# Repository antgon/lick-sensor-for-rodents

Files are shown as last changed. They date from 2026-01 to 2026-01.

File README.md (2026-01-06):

banner

# Lick sensor for rodents

A device for measuring licking behaviour in rodents in real time.

This project describes a lick sensor developed for the purpose of
measuring licking behaviour in laboratory animals. Licking behaviour,
and in particular the analysis of lick microstructure, is a useful tool
for studying ingestive behaviour, motivation, and food preference.

2021-2025 Antonio González

## Features

The lick sensor is built with a Raspberry Pi Pico microcontroller board
and a capacitive touch sensor. It can can be used with standard water
bottles for rodents, and does not require modifications to animal home
cages. The lick sensor can thus be adapted to a wide range of
experimental setups.

Licks are detected in real time with millisecond precision from one or
many drink bottles simultaneously. The data can be recorded using any
standard data acquisition system; it can be sent to a computer for
storage; and/or it can be used for real-time control of additional
laboratory hardware such as LEDs for optogenetics.

Overview of lick sensor

### Variants

Different variants of the lick sensor are possible, depending on the
number of drink bottles required, and also on whether lick data is to be
recorded "raw" (i.e. as a continuous vector of on/off, digital data
samples), or saved in the form of lick events (timestamps).

Details of each of these options can be found in the relevant
directories. Briefly,

* [**One bottle, one BNC output**](bottle-x1-bnc-out). This is the
  simplest lick sensor variant: it uses only one drink bottle. Licks
  from this bottle are detected and directed to a BNC connector from
  where they can be recorded with a data acquisition system and/or used
  for driving additional laboratory hardware in real time.

* [**Several bottles, BNC outputs**](bottle-x6-bnc-out). Similar to the
  setup above but using more than one drink bottle.

* [**Many bottles (up to 12), USB output**](bottle-x12-usb-out). Here,
  lick events (timestamps) from many drink bottles are detected and sent
  to a computer connected to the microcontroller with a USB cable. The
  construction of this lick sensor is very simple and a data-acquisition
  system is not required. On the other hand, the software side of it is
  more elaborate: it is necessary to install and run Python software in
  the host computer.

* [**Many bottles (up to 24), USB output**](bottle-x24-usb-out). As
  above, but using 2 touch-detection boards to handle up to 24 drink
  bottles simultaneously.

## Requirements

### Lick sensor hardware

* Drinking bottle(s). Any standard drinking bottle for rodents should
  work. We use the Crystal Deluxe Mini Bottle 75 ml ([Classic Pet
  Products, UK, cat. num.
  0190](https://classicpetproducts.co.uk/product/crystal-deluxe-mini-bottle-75ml/))
  obtained from a local pet shop.
* [Raspberry Pi
  Pico](https://www.raspberrypi.com/products/raspberry-pi-pico)
  microcontroller board.
* Capacitive touch sensor module. We use [Adafruit product ID
  1982](https://www.adafruit.com/product/1982); up to 12 water bottles
  can be connected to one of these modules[^1]. Other manufacturers sell
  touch sensors based on the MPR121 and any of these should work equally
  well.
* Stranded-core cable (e.g. 24 AWG or 26 AWG standard hook-up cable).
* A USB cable for the Raspberry Pi Pico.
* BNC connector(s). Optional, depending on the sensor variant chosen.

Some means to put the components together, for example:

* Perforated board or stripboard.
* Jumper wires.
* Soldering tools.

Supplier information and ordering codes are listed in
[material.md](docs/material.md).

### Lick sensor software

* C development tools and the knowledge/ability to build a project for
  the Raspberry Pi Pico, as described in the [Pico
  documentation](https://datasheets.raspberrypi.com/pico/getting-started-with-pico.pdf).
* MPR121 library for the Raspberry Pi Pico, available at
  https://github.com/antgon/pico-mpr121.

### Data acquisition hardware

Depending on the variant chosen, you will need either:

* A standard laboratory data-acquisition system. This is only needed
  if you want to record *raw* data (e.g.
  [bottle-x1-bnc-out](bottle-x1-bnc-out)), or
* A computer to record lick events. We use a Raspberry Pi 4 computer
  with very good results. See [bottles-x12-usb-out](bottles-x12-usb-out)
  for details.

[^1]: Adafruit sell two different MPR121 touch sensor breakouts under
    the same Product ID 1982: the original, header-only version, and the
    STEMMA QT version. Both work in the same way, and the PCBs are the
    same size (and look similar). Be aware, however, that **the pins are
    in a different order**.

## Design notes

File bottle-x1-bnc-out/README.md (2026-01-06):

# Lick sensor: one bottle, BNC output

Lick sensor for one drinking bottle, with continuous raw output stream.

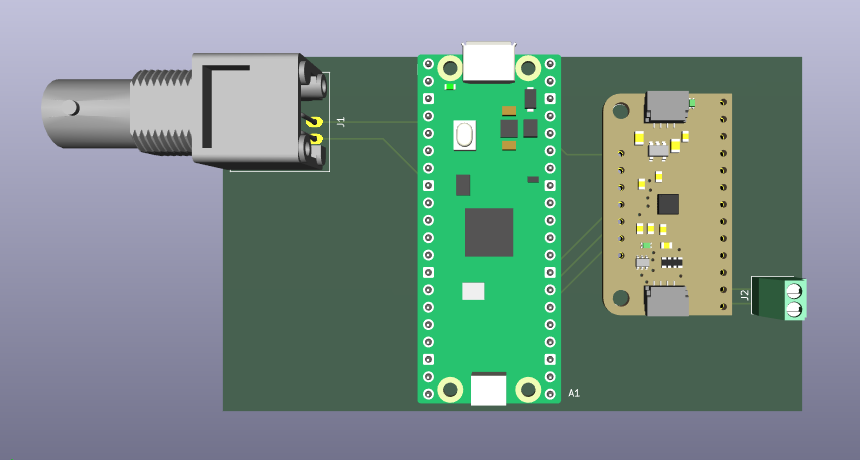
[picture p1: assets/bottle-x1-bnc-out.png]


## Description

This version of the lick sensor is simple to build and operate.

Lick data from the sensor is sent to the BNC connector as a stream of
digital values. A data acquisition board can be connected to this BNC in
order to capture licking data.

Alternatively, the output from the BNC connector can be used to control
some additional piece of laboratory hardware. For example, an LED for
optogenetics connected to the lick sensor in this manner would be
switched on or off according to licks. 

## Material

The components can be mounted and connected using a stripboard. Other
than that, all is needed is

* BNC connector
* Raspberry Pi Pico
* Touch sensor breakout board MPR121
* Terminal block (02x01) or similar

Detailed wiring diagrams are in the folder [pcb](pcb).

## Programming and operation

* Compile `lick_gpio_single.c` and flash into the Pico.
* Connect the spout of a drinking bottle to the terminal block. If only
  one cable is used (i.e. signal only, no ground) make sure to connect
  this to the side of the terminal block that is in turn connected to
  the input `0` in the touch sensor breakout board.
* Power up the Pico (e.g. using a USB cable).
* Connect data acquisition board and/or additional hardware to the BNC
  connector.

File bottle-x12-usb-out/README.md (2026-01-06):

# Lick sensor: up to 12 bottles, detect lick events

This variant of the sensor detects licks from up to 12 drink bottles
simultaneously. Lick events (timestamps) are sent to a host computer
connected to the Raspberry Pi Pico via a USB cable.

## Wiring and operation

Wiring of the components is simple and a stripboard can be used to
facilitate this; see folder [pcb](pcb).

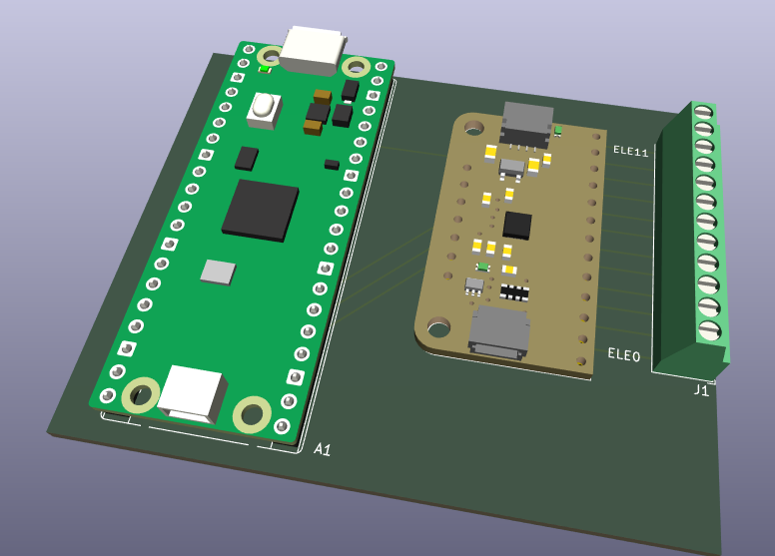
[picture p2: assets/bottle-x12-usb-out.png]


For logging the data, a host computer connected to the lick sensor must
read and save the data received. We use for that a Raspberry Pi 4 (or 5)
computer:

* Compile `lick_events_usb.c` and flash into the Pico.
* Save the provided Python script (`lick_events_reader.py`) to the host
  computer.
* Connect the drink bottles to the lick sensor.
* Connect the Pico to the host computer.
* Boot the host computer. Open a terminal and run the Python script
  above. Lick data will be logged to a local text file. To stop, press
  Ctrl+C.
* To convert the data in the text file to a more readable form suitable
  for analysis, run the Python script
  [`events-to-long.py`](../utils/events-to-long.py).

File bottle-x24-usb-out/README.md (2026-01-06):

# Lick sensor: up to 24 bottles, log lick events

This variant of the sensor detects licks from up to 24 drink bottles
simultaneously. A host computer connected to the sensor logs lick events
(timestamps).

The principles are the same as in the [12-bottle
variant](../bottle-x12-usb-out/) but this variant requires 2
touch-sensing breakout boards.

## Wiring and operation

All components fit on a 100x75 stripboard. The figures below illustrate
how these components can be connected taking advantage of the copper
strips on the board (horizontal) and jumper wires (vertical); see
diagrams in the folder [pcb](pcb).

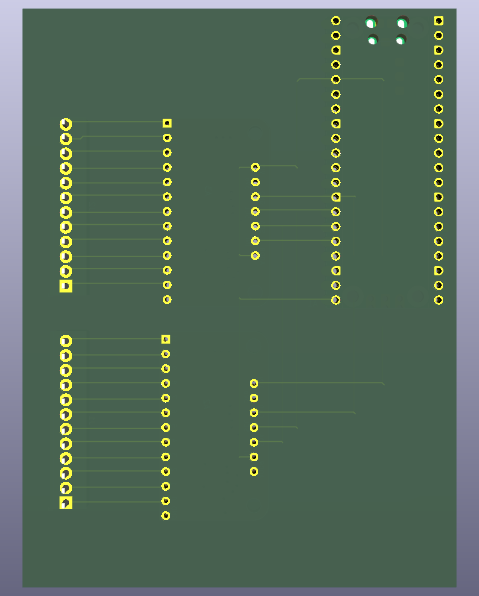
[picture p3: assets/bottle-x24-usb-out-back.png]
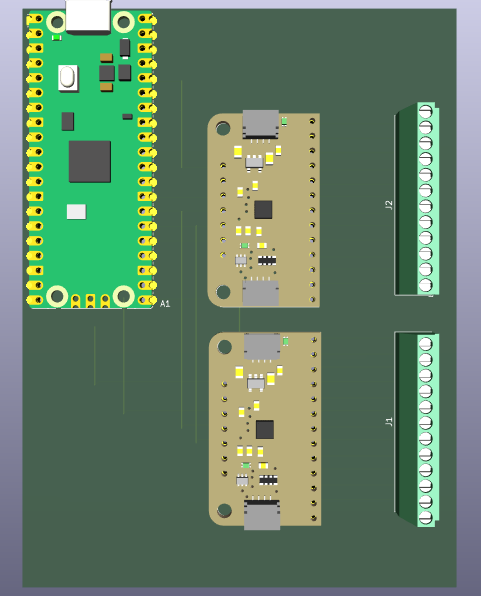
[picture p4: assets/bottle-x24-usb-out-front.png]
|<br>Back|<br>Front|
|:-:|:-:|

For logging the data, a host computer connected to the lick sensor must
read and save the data received. We use for that a Raspberry Pi 4 (or 5)
computer:

* Compile [`lick_two_sensors.c`](lick_two_sensors.c) and flash into the
  Pico.
* Save the Python script
  [`lick_events_reader.py`](`lick_events_reader.py`) to the host
  computer.
* Connect the drink bottles to the lick sensor.
* Connect the Pico to the host computer.
* Boot the host computer. Open a terminal and run the Python script
  above. Lick data will be logged to a local text (csv) file. To stop,
  press Ctrl+C.

## Data post-processing

By default, the data sent by the Pico to the computer is saved as a text
(csv) file consisting of the timestamp of the lick event(s) followed by
a single number for each of the 2 touch sensors. That number is the
binary representation of the status of the sensor's electrodes; thus,
for example, if licks were detected by electrodes 0 and 4 in sensor A,
the number logged for that sensor will be 17 (0b000_0001_0001).

To extract the values for each electrode from that data file for further
analysis, the csv file can be further processed off-line with the script
[`events-to-long.py`](../utils/events-to-long.py).

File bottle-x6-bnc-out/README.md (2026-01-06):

# Lick sensor: several bottles, BNC outputs

Lick sensor for more than one drinking bottle, with continuous raw
output stream.

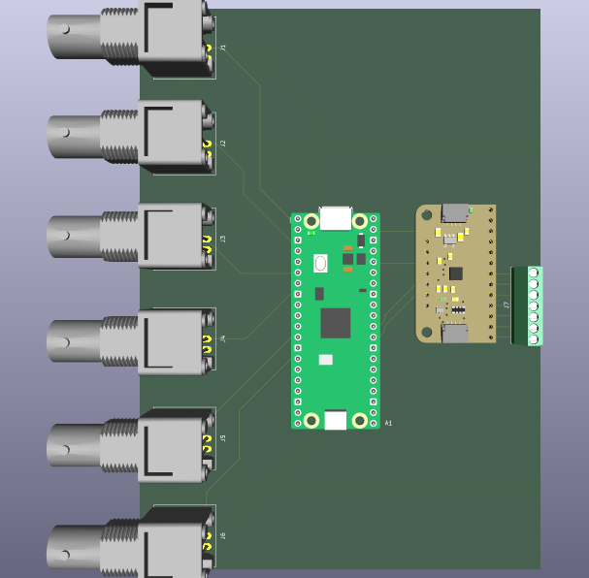
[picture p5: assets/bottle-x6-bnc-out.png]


## Description

This is an extension of the lick sensor used for only one bottle
([bottle-x1-bnc-out](../bottle-x1-bnc-out)), and programming and
operation is thus similar as described there.

Wiring details are in the folder [pcb](pcb).

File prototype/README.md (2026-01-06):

# Lick sensor prototype

This prototype was designed for testing the lick sensor while observing
the effects of changing the sensor's settings: an LCD and four push
buttons allow to change the settings of the MPR121 capacitive sensor on
the fly. This helps tune the sensor and evaluate its ability to detect
licks under varying circumstances.

There are two BNC connectors: one outputs the digital signal, i.e. 0s
and 1s, with 1s indicating licks. The other outputs the analog signal
from the capacitive sensor, which helps visualise the changes in
capacitance that occur with licking. With these two outputs connected to
a data acquisition board, the behaviour of the touch sensor can be
assessed.

lick-sensor-board

## Building and operation

1. This prototype is designed to be built on a perforated board. Details
   can be found in the [pcb](pcb) folder.

2. Program the microcontroller: compile `app/main.c` and flash into the
   Raspberry Pi Pico. See the [Pico
   documentation](https://www.raspberrypi.com/documentation/microcontrollers/pico-series.html#documentation)
   for details of how to do this. Note that in addition to standard Pico
   libraries, these 3 libraries are required:
    * [lcd16x2_i2c.h](https://github.com/antgon/pico-lcd16x2_i2c)
    * [mcp48x1.h](https://github.com/antgon/pico-mcp48x1)
    * [mpr121.h](https://github.com/antgon/pico-mpr121)

3. Connect a drink bottle to the board. Connect the two BNC outputs to a
   data acquisition (DAQ) board. Power up the Raspberry Pi Pico. The
   lick sensor will output data to the BNCs every 20 ms (50 Hz).

4. Modify the MCP121 settings using the buttons (see [docs](docs)
   for detailed instructions), use the DAQ to observe the effects of
   doing this.

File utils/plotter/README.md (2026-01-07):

Banner

<h2 align="center">
Read and plot serial data from a microcontroller
</h2>

* * *

**microPyGraph** displays serial data in real time. It is intended as a
simple way to plot data from a microcontroller. It is not very efficient
in the way resources are used, as it just repeatedly reads ascii from
the serial port `print`ed line-by-line by the microcontroller, but it
helps to quickly evaluate microcontroller-acquired data values with
minimal effort.

## Requirements

* [NumPy](https://numpy.org/)
* [PyQtGraph](http://pyqtgraph.org/)
* [pySerial](https://github.com/pyserial/)

## Usage

1. Program the microcontroller for sending data over the serial port
   (typically with `print` or `printf`; see examples below) separated by
   a space at regular intervals.

1. Connect the microcontroller to the host computer.

1. Run `python main.py` on the host computer. (Or, if `uv` is installed
   in the host computer, do `uv run main.py`.)

1. Click the "play" button to display the data.

### Example 1: Sample analog data and plot in real time

A light-dependent resistor (aka photoresistor) was connected to a
Raspberry Pico (adc pin 26) in order to measure the relative intensity
of ambient light. The following micropython code was set to read and
print the measured voltage every 500 ms:

```python
from machine import ADC
import utime

conversion_factor = 3.3/(2**16-1)

# Light-dependent resistor
ldr = ADC(26)

while True:
    ldr_adc_val = ldr.read_u16()
    ldr_voltage = ldr_adc_val * conversion_factor
    print(ldr_voltage)
    utime.sleep_ms(500)
```

Running `python microdaq.py` on the host computer and clicking the
"play" button shows the data in real time. In this example the y-axis
units are volts (as established in the micropython code above when adc
values are converted to voltage before printing).

### Example 2: Plot more than one signal

More that one signal can be plotted simultaneously by just setting the
microcontroller to print more than one value as needed. In this example,
one (analog) thermometer was connected to adc pin 28 on the same
Raspberry Pico as above. The micropython code is now:

```python
from machine import ADC
import utime

conversion_factor = 3.3/(2**16-1)

# Light-dependent resistor
ldr = ADC(26)

# Thermometer (TPM37, analog)
tmp37 = ADC(28)

while True:
    tmp37_adc_val = tmp37.read_u16()
    tmp37_voltage = tmp37_adc_val * conversion_factor
    tmp37_temperature = tmp37_voltage/0.02

    ldr_adc_val = ldr.read_u16()
    ldr_voltage = ldr_adc_val * conversion_factor

    print(tmp37_temperature, ldr_voltage)

    utime.sleep_ms(500)
```
**microPyGraph** will detect and plot the two signals. Here, the top
trace is the ambient temperature (in degrees C) and the bottom trace is
the relative ambient light intensity (in volts).

### Example 3: Using with Arduino

To test on an Arduino, the following code was uploaded to an Arduino
Uno. The two values must be printed on the same line, separated by a
space:
```c
void setup() {
  Serial.begin(9600);
}

float value = 0;
int direction = 1;
const float interval = 0.1;

void loop() {
  Serial.print(value);  // Print the first value
  Serial.print(' ');  // Print a space to separate the values
  Serial.println(sin(value));  // Print the second value and end the line
  value += (interval * direction);
  if ((value < -PI) | (value > PI)) {
    direction *= -1;
  }
  delay(50); // in ms
}
```
(This same code works for other microcontrollers that can be used with
the Arduino IDE, e.g. Adafruit Feather.)

Note that for this Arduino example to work a different baud rate may
have to be set in `main.py`. (The default baud rate in that file should
work just fine for the Raspberry Pi Pico.)

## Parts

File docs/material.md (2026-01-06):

# Material

## Main components

Item | Supplier | Order code
-----|----------|-----------
Raspberry Pi Pico 2 microcontroller | Farnell | 4531086
MPR121 capacitive touch sensor breakout, Adafruit 1982 | DigiKey | 1528-1038-ND
MPR121 capacitive touch sensor breakout, Adafruit 1982 | The PiHut |ADA1982
Stripboard 100x100mm | Farnell | 2503759

> [!IMPORTANT]
> Adafruit sell two different MPR121 touch sensor breakouts under the
same Product ID 1982: the original, header-only version, and the STEMMA
QT version. Both work in the same way, and the PCBs are the same size
(and look similar). Be aware, however, that the order of the pins differ
between these two boards.

## Connectors

Item | Supplier | Order code
-----|----------|-----------
Terminal block, 12 way | Farnell | 2776441
BNC socket, right angle, PCB mount | Farnell | CN21972
Pin header, 20 contacts | Farnell | 1668514
PCB receptacle, 8 contacts  | Farnell | 1668100
PCB receptacle, 5 contacts  | Farnell | 3550818
PCB receptacle, 7 contacts  | Farnell | 3660693
PCB receptacle, 20 contacts | Farnell | 1668107

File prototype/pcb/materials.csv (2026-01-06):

Item | Qty | Supplier | PartNum
BNC connector right angle | 2 | Farnell | CN21972
Capacitor 0.1u | 1
Capacitor 10u tantal | 1
Capacitor 1u | 1
Connector 01x04 Pin | 1
Connector 01x04 Socket | 1
DAC MCP4821 | 1 | Farnell | 1439411
IC socket DIL 8 way | 1 | Farnell | SPC15494
LCD SeeedStudio Grove 16x2 I2C | 1 | RapidElectronics | 75-1088
M2 spacers | 2 | Farnell | PC02805
Push button | 4
Raspberry Pi Pico | 1
Stripboard 160x100 | 1 | Farnell | 3263921
Terminal block 01x04 | 1
Touch sensor breakout board MPR121 (Adafruit 1982) | 1 | The PiHut | ADA1982

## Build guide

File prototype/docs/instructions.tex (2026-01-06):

\documentclass[a4paper,11pt]{article}
% Fontsizes: normalsize, small, footnotesize, scriptsize, tiny

%% ++ Language ++

\usepackage{polyglossia}
\setdefaultlanguage[variant=british]{english}

%% ++ Layout ++

\frenchspacing
% \usepackage{setspace}\onehalfspacing
\usepackage[a4paper,margin=3cm]{geometry}
\setlength{\footskip}{1cm}

% To move the title up and reduce space between the date and the first
% paragraph (does not work with KOMA scrartcl),
\usepackage{titling}
\setlength{\droptitle}{-5\baselineskip}
% \predate{\begin{center}\large}
\postdate{\par\end{center}\vspace{-3\baselineskip}}

% To decrease space between sections (does not work with KOMA scrartcl),
% \usepackage[compact]{titlesec} 

%% ++ Figures ++

\usepackage{graphicx}
\usepackage{svg}
\usepackage[off]{svg-extract}
\svgsetup{clean=true,inkscapearea=page,inkscapepath=svg-inkscape/}
\graphicspath{{img/}}
\svgpath{{svg/}}

%% ++ Captions ++

\usepackage{caption}
\captionsetup{format=plain, font={small,singlespacing},
  labelfont=bf, labelsep=period}
    %labelsep=newline, justification=RaggedRight}

%% ++ Lists ++

\usepackage{enumitem}
\setlist{noitemsep}

% ++ Fonts

\usepackage{fontspec}
\usepackage{unicode-math}
\unimathsetup{math-style=ISO}%,warnings-off={mathtools-colon}}
\defaultfontfeatures{Mapping=tex-text}
\setmainfont{TeX Gyre Heros}
%\setmathfont{TeX Gyre Schola Math}[Scale=MatchLowercase]
\setsansfont{TeX Gyre Heros}[Scale=MatchLowercase]
\setmonofont{TeX Gyre Cursor}[Scale=MatchLowercase]
\usepackage{relsize}

%% ++ Headers/footers

\usepackage{fancyhdr}
\usepackage{scrdate}
\pagestyle{fancy}
\renewcommand{\headrulewidth}{0pt}
\fancyhf{}
\fancyfoot[L]{\tiny Antonio González, Ver.~\ISOToday}
\fancyfoot[R]{\thepage}

%% ++ Optional extra formatting

% Remove sections numbering
\setcounter{secnumdepth}{-1}

% Maths. \begin{equation} or \begin{align}
% \usepackage{mathtools}

%% ++ Hyperref
\usepackage{hyperref}
\hypersetup{
  pdfauthor={JA González},
  pdftitle={Lick sensor},
  pdfsubject={},
  hidelinks
}
\urlstyle{same}
% \newcommand\email[1]{\href{mailto:#1}{#1}}

%% ++ Begin
\title{\textbf{Lick sensor}}
%\author{JA González}
\date{}

\begin{document}
\maketitle
\thispagestyle{fancy}
% \vskip-4em

\begin{figure}[h]
    % \centering
    \includesvg[pretex=\footnotesize,width=\columnwidth]{board}
    \caption{Overview of the lick-sensing device.}\label{fig:device}
    \end{figure}

\section{Wiring}
\begin{enumerate}
    \item Use a cable to connect input ``0'' (second from left to right
    on the ``Lick sensor connector'', see Fig.~\ref{fig:device}) to the
    (metal) spout of a drinking bottle (Fig.~\ref{fig:shielding}A).
    \item Connect ``Digital out'' to your data acquisition system with a
    BNC cable.
    \item (Optional) Connect ``Analog out'' to your data acquisition
    system with a BNC cable.
    \item Connect a USB cable to ``USB''. This powers the device. Do
    this only after all other cables have been connected and the
    drinking bottle is in place.
\end{enumerate}

\section{Operation}
\begin{enumerate}
    \item Record data from ``Digital out''. This will be the licking
    signal: a step will appear with every lick
    (Fig.~\ref{fig:shielding}B).
    \item (Optional) Record the signal from ``Analog out''. This signal
    increases or decreases with changes in capacitance in the touch
    sensor and it could be useful at some point if we needed to
    troubleshoot the system.
\end{enumerate}

\section{Adjusting settings}

The default settings should work just fine. If some tuning is needed,
each setting on the display can be adjusted using the buttons:

\begin{itemize}
    \item ``Previous'' and ``Next'' take you through the different
        possible settings.
    \item ``+'' and ``−'' increase or decrease the value of the setting
        currently on display.
\end{itemize}

The most relevant settings are perhaps ``Touch threshold'' and ``Release
threshold'': when the analogue signal goes above Touch threshold, a
touch event (i.e.\ a lick) is triggered. When this signal goes below
Release threshold, the event (lick) is considered to have
ended.\footnote{Note that the value of Touch threshold must always be
greater than that of Release threshold.} Thus, these two values set the
sensitivity of the system and introduce hysteresis to limit jitter.

% Increase Touch threshold if the system is too sensitive.
% Increase Release threshold if 

\section{Optional: grounding}

It may be that animals trigger false positive lick events when they
touch with their paw the drinking bottle. These false positive events
may be reduced by shielding the spout of the water bottle with foil
(Fig.~\ref{fig:shielding}C,D) and connecting this foil to ``G'' (ground)
in the Lick sensor connector. Just ensure that signal and ground cables
do not make contact with each other.

\begin{figure}
    \centering
    \includesvg[pretex=\scriptsize,width=\columnwidth]{lickometer-system}
    \caption{(\textbf{A}) A cable connecting the spout of the drinking
    bottle to the lick sensor is all the wiring required at the animal's
    end. (\textbf{B}) The output of the lick sensor (``Digital out'' in
    Fig.~\ref{fig:device}) is a series of voltage steps, each indicating
    a lick event. (\textbf{C}) Optionally, shielding the spout of the
    drinking bottle may help reduce false positives that arise when
    animals hold the spout while drinking. To do this, surround the
    spout with a piece of conductive material (e.g.\ foil) and connect
    this to ground (``G'') on the Lick sensor connector. Use heat shrink
    or similar to ensure that the foil (ground) and the spout (sensor)
    do not touch each other. The tip of the spout should be clear of the
    foil shielding. (\textbf{D}) Keeping ground and signal cables
    separate, connect these the to the lick
    sensor.}\label{fig:shielding}
\end{figure}

\end{document}

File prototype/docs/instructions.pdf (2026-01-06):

## Lick sensor

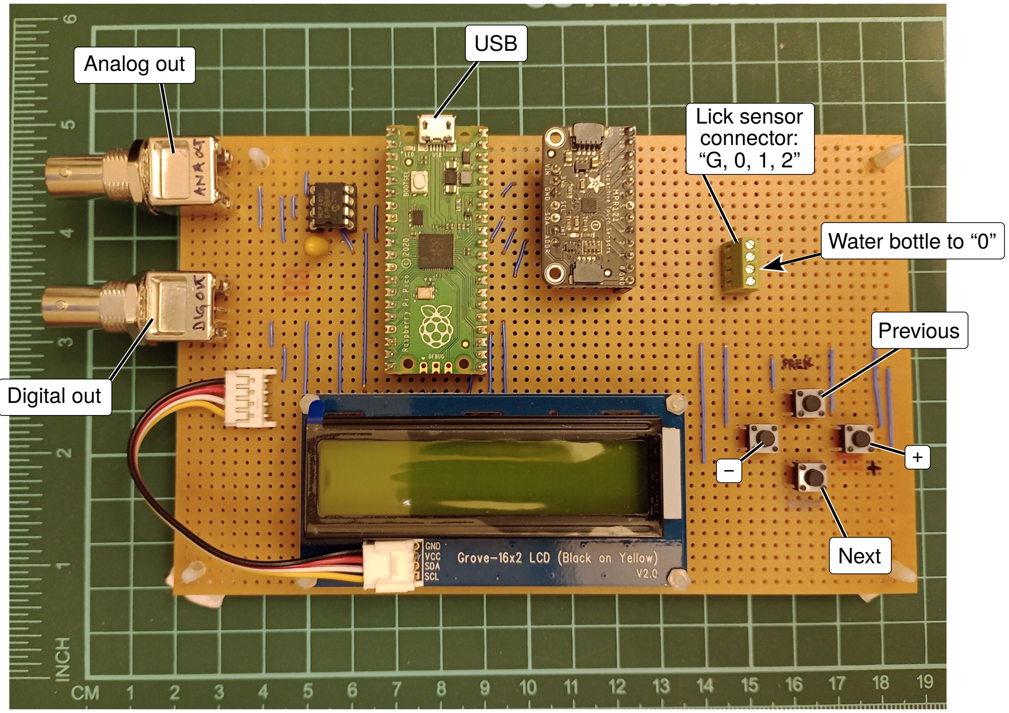
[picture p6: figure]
Previous; Next; Lick sensor connector: “G, 0, 1, 2”; Water bottle to “0”; Digital out; Analog out; USB

Figure 1. Overview of the lick-sensing device.

## Wiring

1. Use a cable to connect input “0” (second from left to right on the “Lick sensor connector”, see Fig. 1) to the (metal) spout of a drinking bottle (Fig. 2A).
2. Connect “Digital out” to your data acquisition system with a BNC cable.
3. (Optional) Connect “Analog out” to your data acquisition system with a BNC cable.
4. Connect a USB cable to “USB”. This powers the device. Do this only after all other cables have been connected and the drinking bottle is in place.

## Operation

1. Record data from “Digital out”. This will be the licking signal: a step will appear with every lick (Fig. 2B).
2. (Optional) Record the signal from “Analog out”. This signal increases or decreases with changes in capacitance in the touch sensor and it could be useful at some point if we needed to troubleshoot the system.
Antonio González, Ver. 2023-12-06 | 1

Spout | Cable (signal)

Cable
(ground)

Heat shrink

Heat shrink

Aluminium foil

C

Ground
(to “G”)

B

0

1

Time

Lick

D

Signal
(to “0”)

A

Signal
(to “0”)

Figure 2. (A) A cable connecting the spout of the drinking bottle to the lick sensor is all the wiring required at the animal’s end. (B) The output of the lick sensor (“Digital out” in Fig. 1) is a series of voltage steps, each indicating a lick event. (C) Optionally, shielding the spout of the drinking bottle may help reduce false positives that arise when animals hold the spout while drinking. To do this, surround the spout with a piece of conductive material (e.g. foil) and connect this to ground (“G”) on the Lick sensor connector. Use heat shrink or similar to ensure that the foil (ground) and the spout (sensor) do not touch each other. The tip of the spout should be clear of the foil shielding.
(D) Keeping ground and signal cables separate, connect these the to the lick sensor.

## Adjusting settings

The default settings should work just fine. If some tuning is needed, each setting on the display can be adjusted using the buttons:

- “Previous” and “Next” take you through the different possible settings.
- “+” and “−” increase or decrease the value of the setting currently on display.

The most relevant settings are perhaps “Touch threshold” and “Release threshold”: when the analogue signal goes above Touch threshold, a touch event (i.e. a lick) is triggered. When this signal goes below Release threshold, the event (lick) is considered to have ended.¹ Thus, these two values set the sensitivity of the system and introduce hysteresis to limit jitter.

## Optional: grounding

It may be that animals trigger false positive lick events when they touch with their paw the drinking bottle. These false positive events may be reduced by shielding the spout of the water bottle with foil (Fig. 2C,D) and connecting this foil to “G” (ground) in the Lick sensor connector. Just ensure that signal and ground cables do not make contact with each other.

1Note that the value of Touch threshold must always be greater than that of Release threshold.

Antonio González, Ver. 2023-12-06 | 2

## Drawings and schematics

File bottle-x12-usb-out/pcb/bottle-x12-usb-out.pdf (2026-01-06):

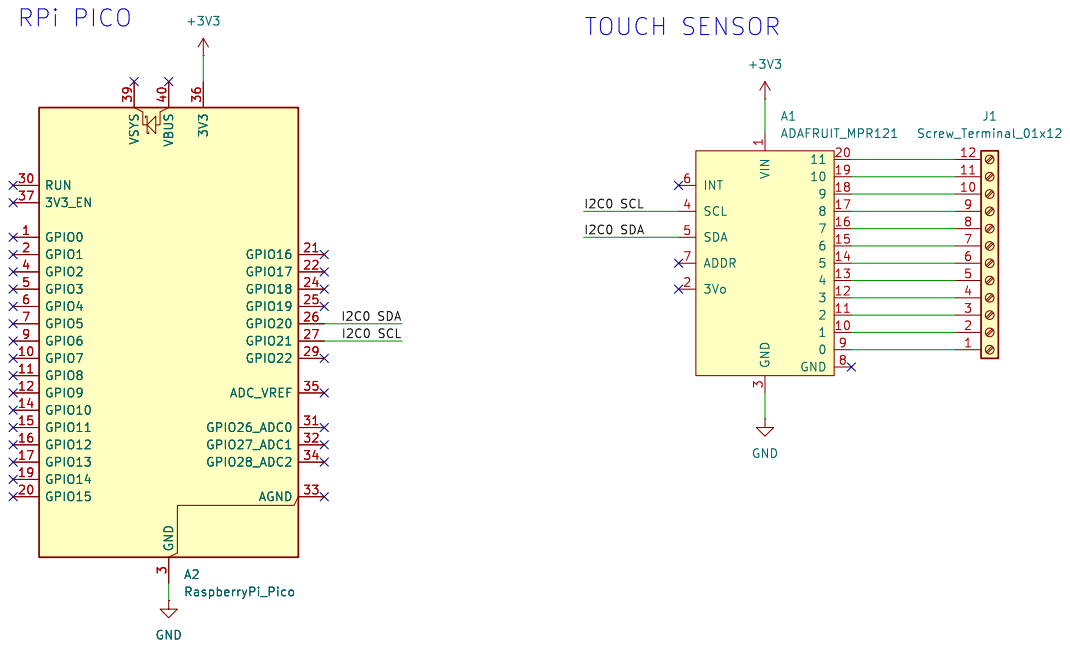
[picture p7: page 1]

Id: 1/1 Title: Lick sensor, 12 bottles, USB output File: bottle-x12-usb-out.kicad_sch Sheet: /

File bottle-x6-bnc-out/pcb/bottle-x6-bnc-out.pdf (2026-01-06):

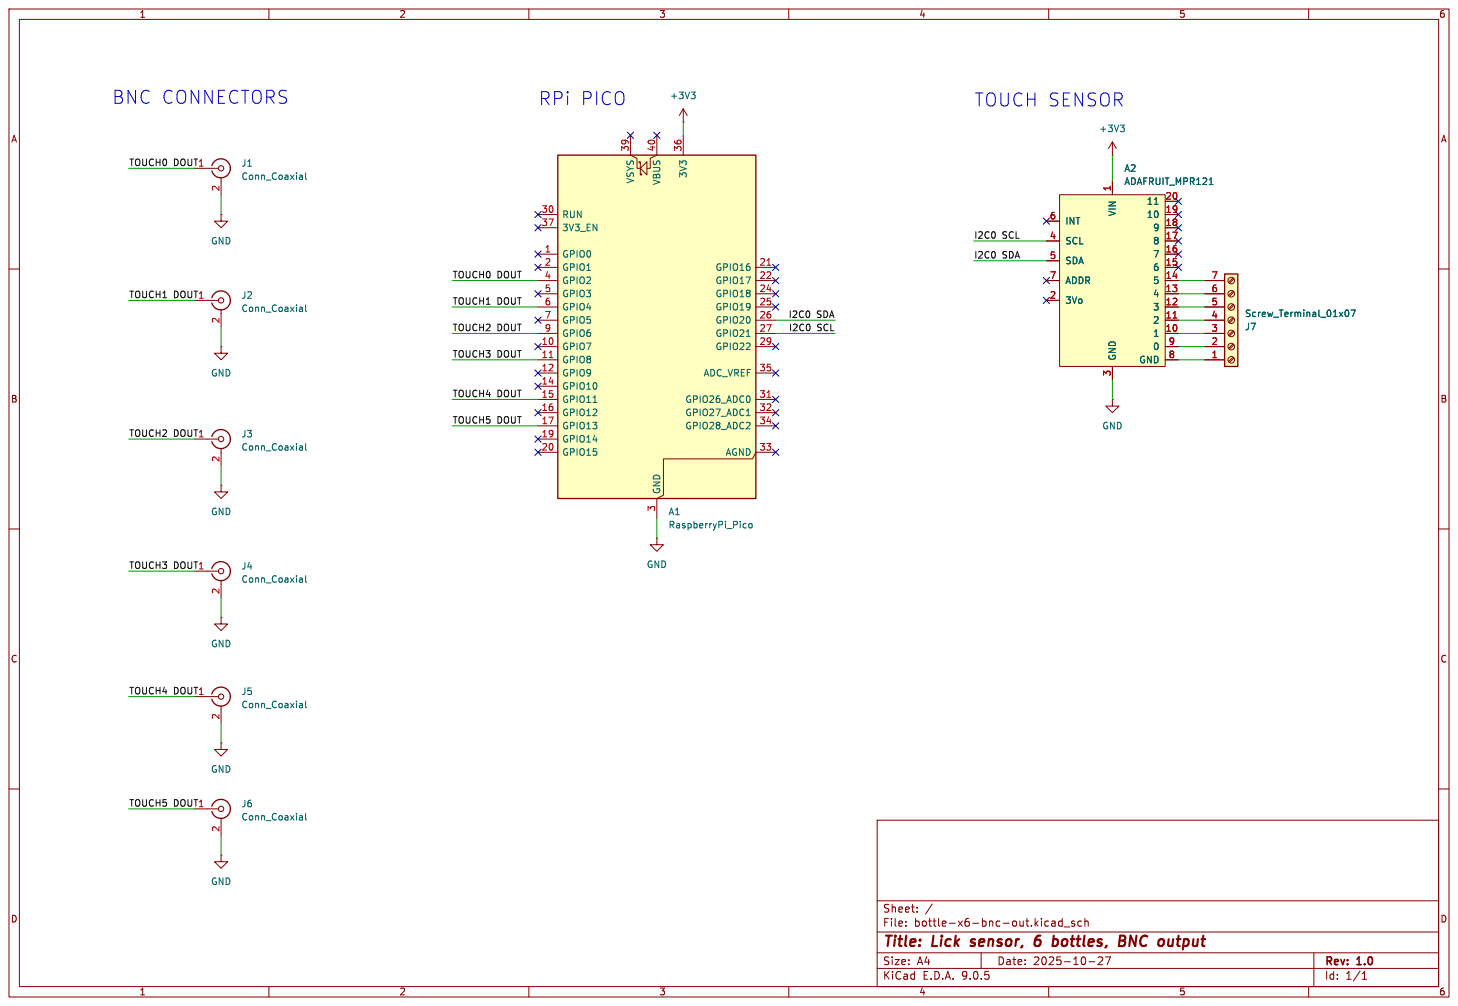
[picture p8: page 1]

Id: 1/1 Title: Lick sensor, 6 bottles, BNC output File: bottle-x6-bnc-out.kicad_sch Sheet: / GND

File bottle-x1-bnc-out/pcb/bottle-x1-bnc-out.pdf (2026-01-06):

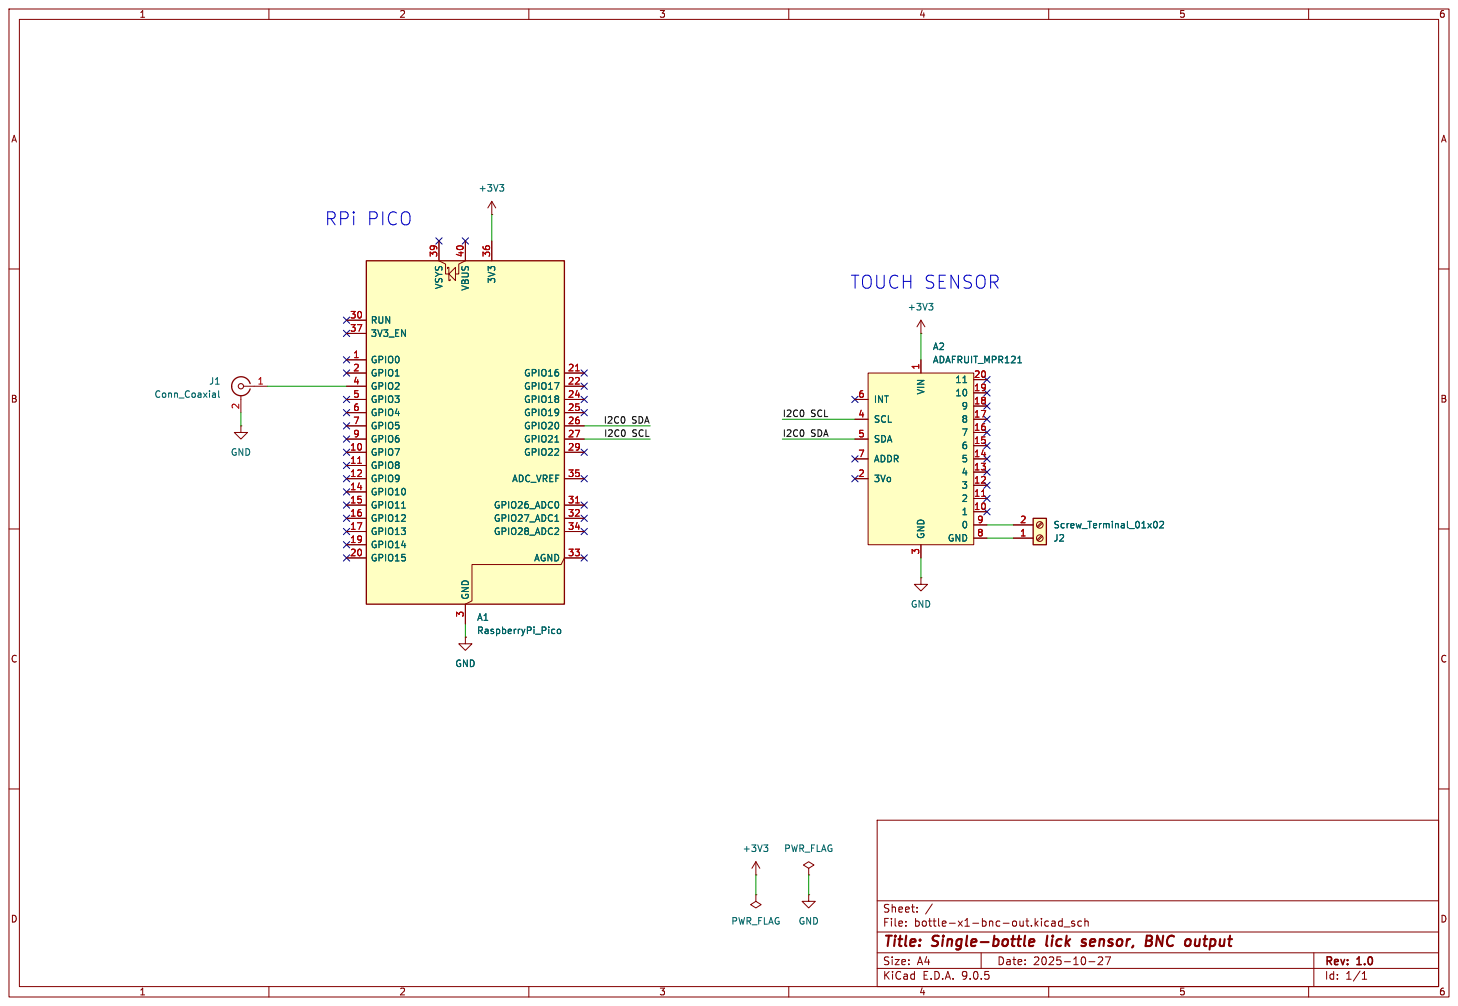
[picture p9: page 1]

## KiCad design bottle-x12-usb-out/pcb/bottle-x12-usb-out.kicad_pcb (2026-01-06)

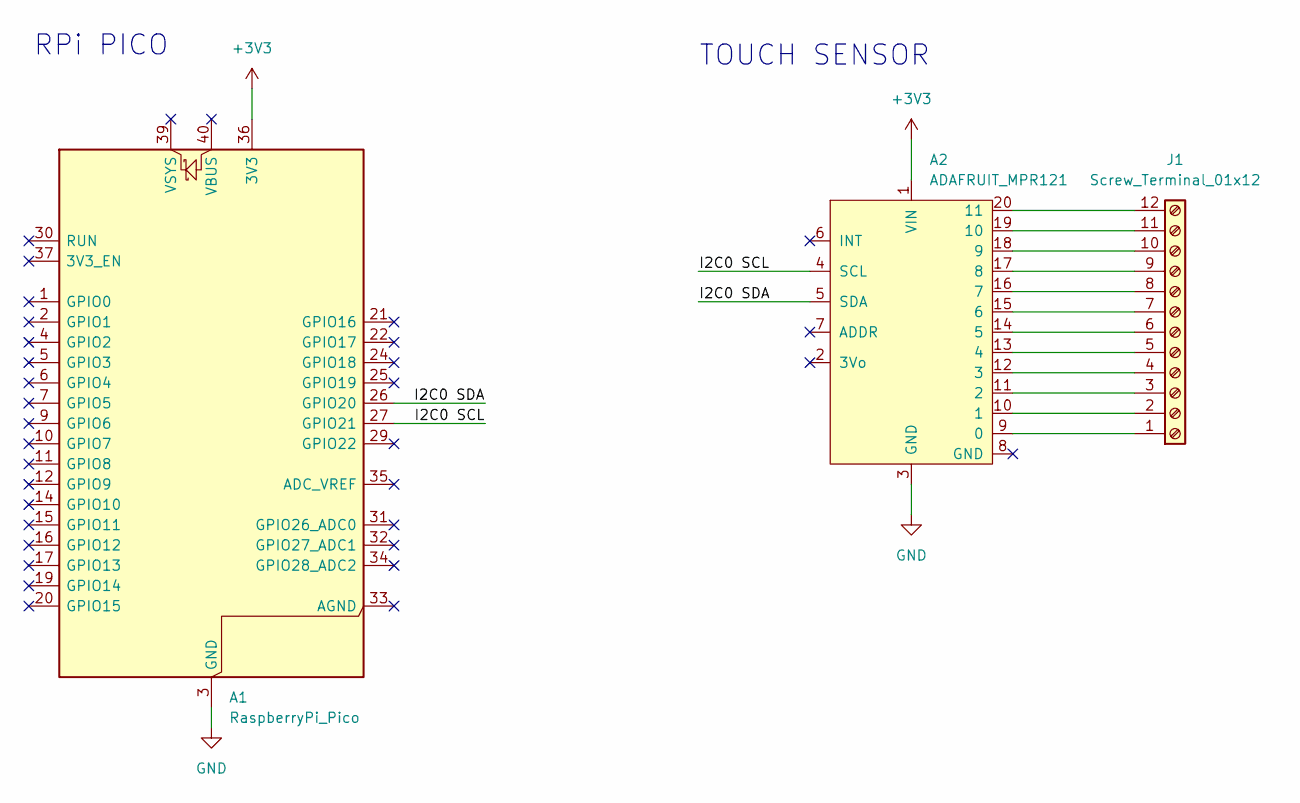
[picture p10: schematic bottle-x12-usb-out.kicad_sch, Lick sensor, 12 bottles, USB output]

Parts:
A1: RaspberryPi_Pico; RaspberryPi_Pico_Common_THT
A2: ADAFRUIT_MPR121
J1: Screw_Terminal_01x12; TerminalBlock_Phoenix_MPT-0,5-12-2.54_1x12_P2.54mm_Horizont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

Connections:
+3V3: A1.36 (3V3), A2.1 (VIN)
/I2C0 SCL: A1.27 (GPIO21), A2.4 (SCL)
/I2C0 SDA: A1.26 (GPIO20), A2.5 (SDA)
GND: A1.3 (GND), A1.8 (GND), A1.13 (GND), A1.18 (GND), A1.23 (GND), A1.28 (GND), A1.38 (GND), A2.3 (GND)
unnamed: A2.9 (0), J1.1
unnamed: A2.10 (1), J1.2
unnamed: A2.11 (2), J1.3
unnamed: A2.12 (3), J1.4
unnamed: A2.13 (4), J1.5
unnamed: A2.14 (5), J1.6
unnamed: A2.15 (6), J1.7
unnamed: A2.16 (7), J1.8
unnamed: A2.17 (8), J1.9
unnamed: A2.18 (9), J1.10
unnamed: A2.19 (10), J1.11
unnamed: A2.20 (11), J1.12

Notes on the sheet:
TOUCH SENSOR
RPi PICO

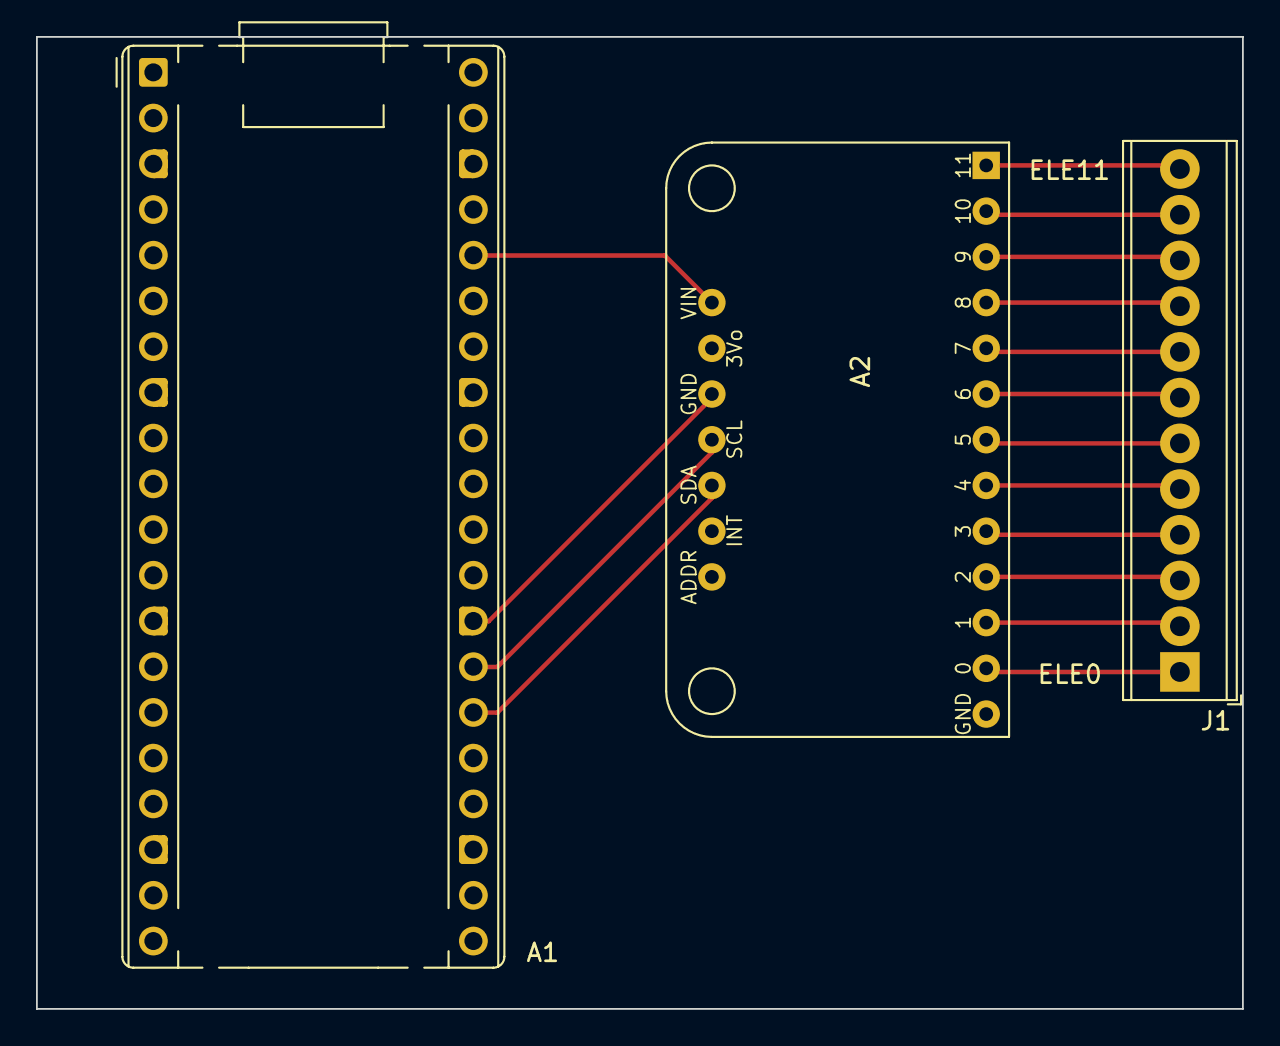
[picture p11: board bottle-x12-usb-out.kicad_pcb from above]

Board: 2 copper layers, 67.0 x 54.0 mm, 3 parts (0 on the bottom side), 16 nets.

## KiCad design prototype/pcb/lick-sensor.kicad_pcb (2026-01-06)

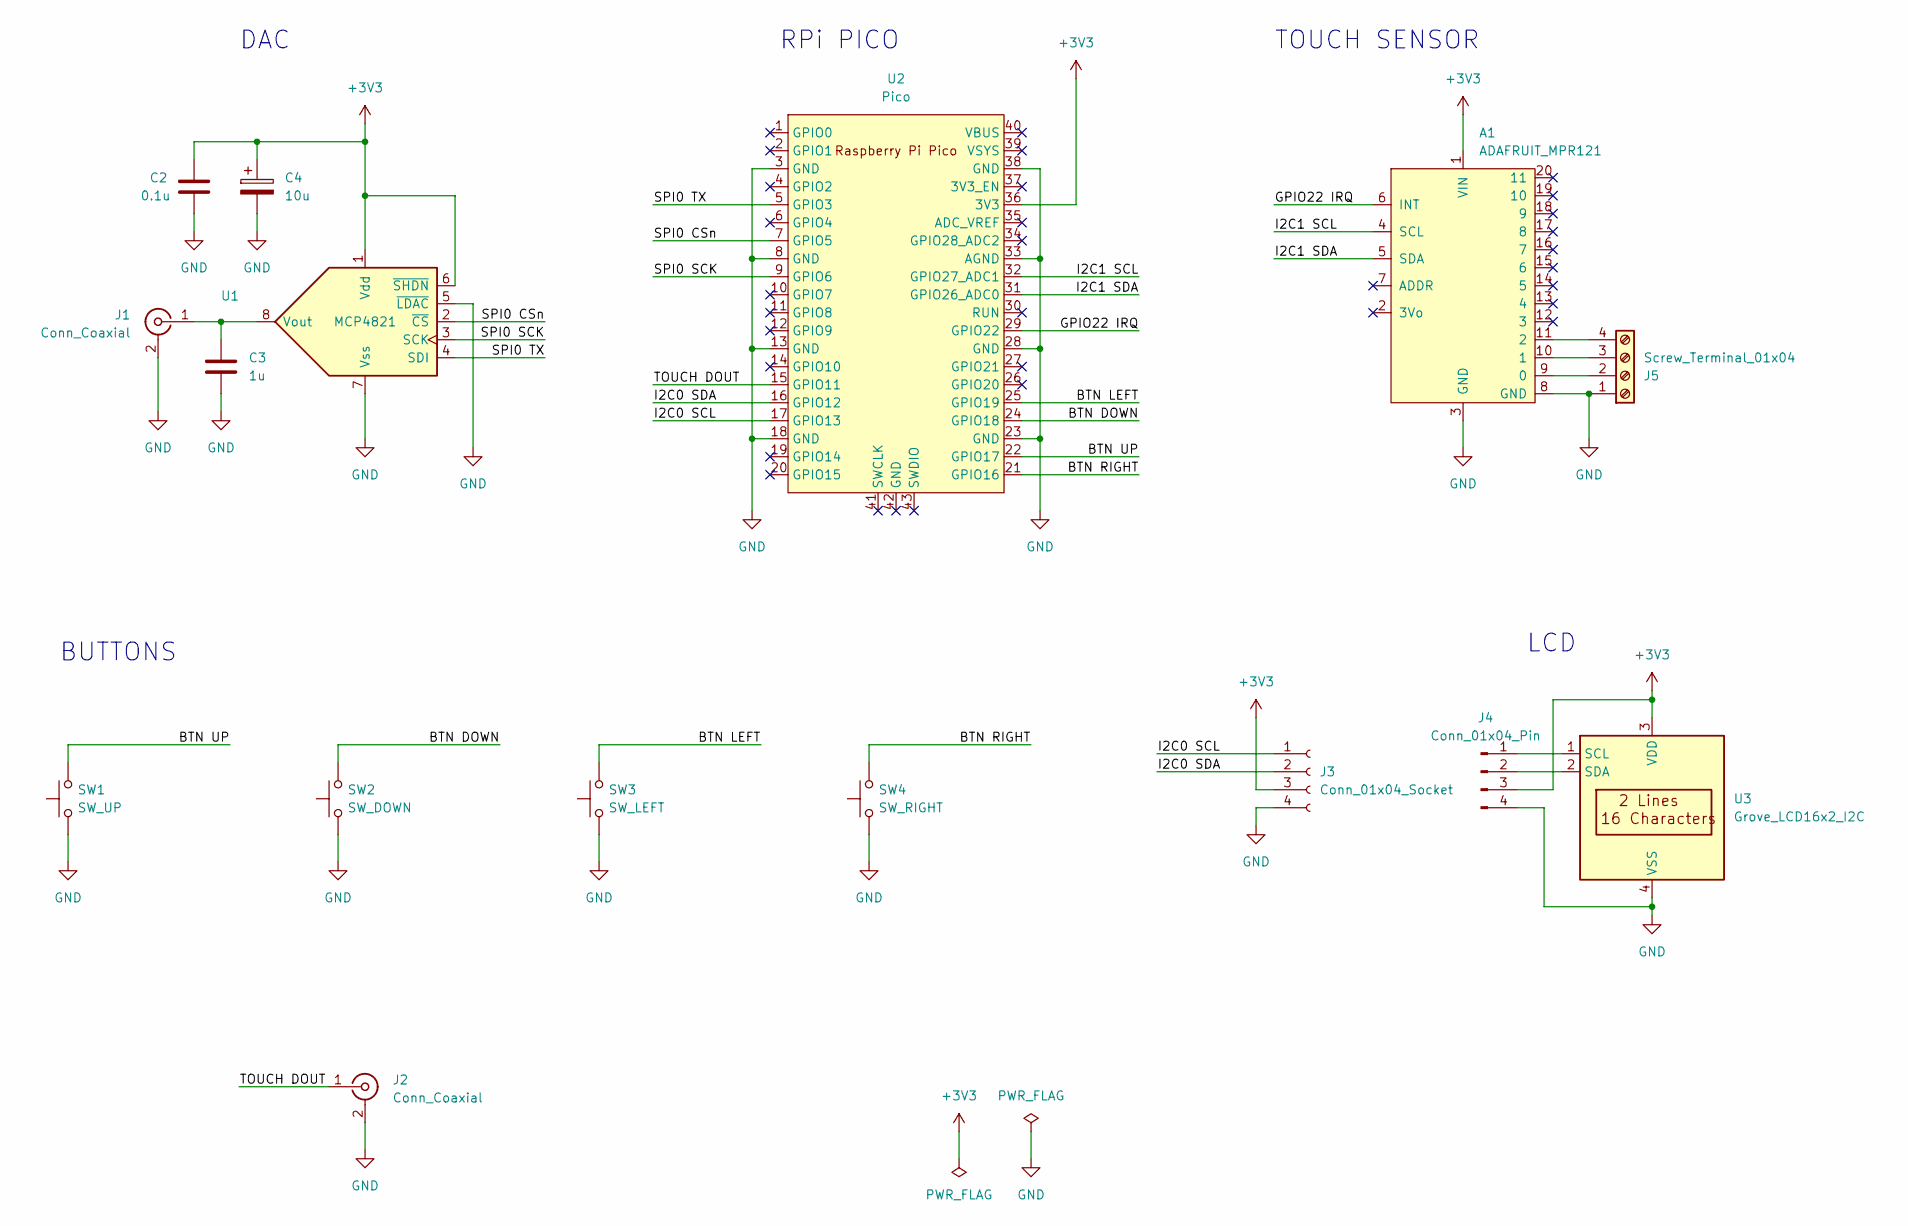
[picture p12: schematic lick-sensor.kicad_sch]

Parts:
A1: ADAFRUIT_MPR121
C2: 0.1u; C_Disc_D5.0mm_W2.5mm_P2.50mm
C3: 1u; C_Disc_D5.0mm_W2.5mm_P2.50mm
C4: 10u; CP_Radial_Tantal_D5.0mm_P2.50mm
J1, J2: Conn_Coaxial; BNC_Amphenol_B6252HB-NPP3G-50_Horizontal
J3: Conn_01x04_Socket; Molex_Nano-Fit_105313-xx04_1x04_P2.50mm_Horizontal
J4: Conn_01x04_Pin; Molex_Nano-Fit_105313-xx04_1x04_P2.50mm_Horizontal
J5: Screw_Terminal_01x04; TerminalBlock_Phoenix_MPT-0,5-4-2.54_1x04_P2.54mm_Horizontal
SW1: SW_UP; SW_PUSH_6mm
SW2: SW_DOWN; SW_PUSH_6mm
SW3: SW_LEFT; SW_PUSH_6mm
SW4: SW_RIGHT; SW_PUSH_6mm
U1: MCP4821; DIP-8_W7.62mm
U2: Pico; RPi_Pico_SMD_TH
U3: Grove_LCD16x2_I2C

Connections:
+3V3: A1.1 (VIN), C2.1, C4.1, J3.3, J4.3, U1.1 (Vdd), U1.6 (~SHDN), U2.36 (3V3), U3.3 (VDD)
/BTN DOWN: SW2.2, U2.24 (GPIO18)
/BTN LEFT: SW3.2, U2.25 (GPIO19)
/BTN RIGHT: SW4.2, U2.21 (GPIO16)
/BTN UP: SW1.2, U2.22 (GPIO17)
/GPIO22 IRQ: A1.6 (INT), U2.29 (GPIO22)
/I2C0 SCL: J3.1, U2.17 (GPIO13)
/I2C0 SDA: J3.2, U2.16 (GPIO12)
/I2C1 SCL: A1.4 (SCL), U2.32 (GPIO27_ADC1)
/I2C1 SDA: A1.5 (SDA), U2.31 (GPIO26_ADC0)
/SPI0 CSn: U1.2 (~CS), U2.7 (GPIO5)
/SPI0 SCK: U1.3 (SCK), U2.9 (GPIO6)
/SPI0 TX: U1.4 (SDI), U2.5 (GPIO3)
/TOUCH DOUT: J2.1 (In), U2.15 (GPIO11)
GND: A1.3 (GND), A1.8 (GND), C2.2, C3.2, C4.2, J1.2 (Ext), J2.2 (Ext), J3.4, J4.4, J5.1, SW1.1, SW2.1, SW3.1, SW4.1, U1.5 (~LDAC), U1.7 (Vss), U2.3 (GND), U2.8 (GND), U2.13 (GND), U2.18 (GND), U2.23 (GND), U2.28 (GND), U2.33 (AGND), U2.38 (GND), U3.4 (VSS)
unnamed: A1.9 (0), J5.2
unnamed: A1.10 (1), J5.3
unnamed: A1.11 (2), J5.4
unnamed: C3.1, J1.1 (In), U1.8 (Vout)
unnamed: J4.1, U3.1 (SCL)
unnamed: J4.2, U3.2 (SDA)

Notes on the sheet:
BUTTONS
TOUCH SENSOR
LCD
DAC
RPi PICO

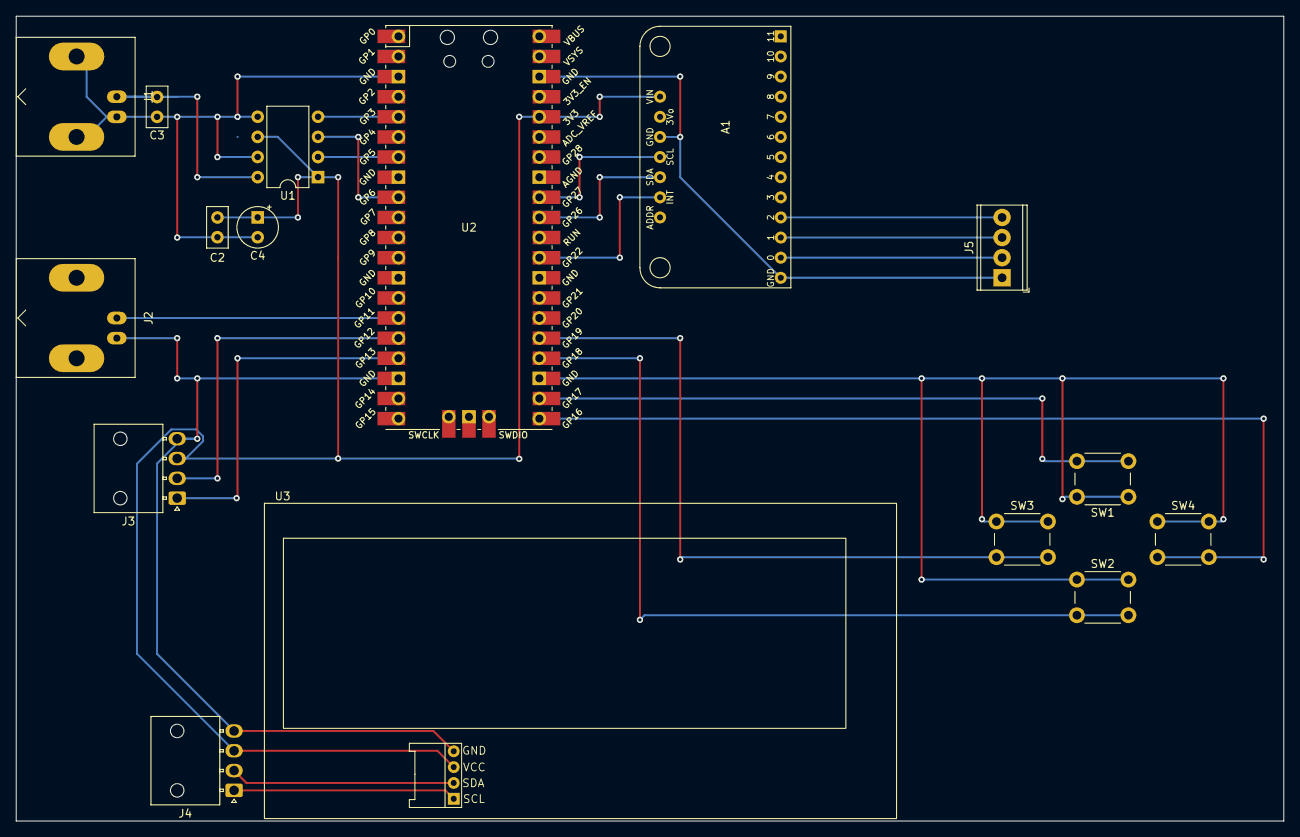
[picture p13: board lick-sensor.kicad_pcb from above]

Board: 2 copper layers, 160.0 x 101.6 mm, 16 parts (0 on the bottom side), 21 nets.

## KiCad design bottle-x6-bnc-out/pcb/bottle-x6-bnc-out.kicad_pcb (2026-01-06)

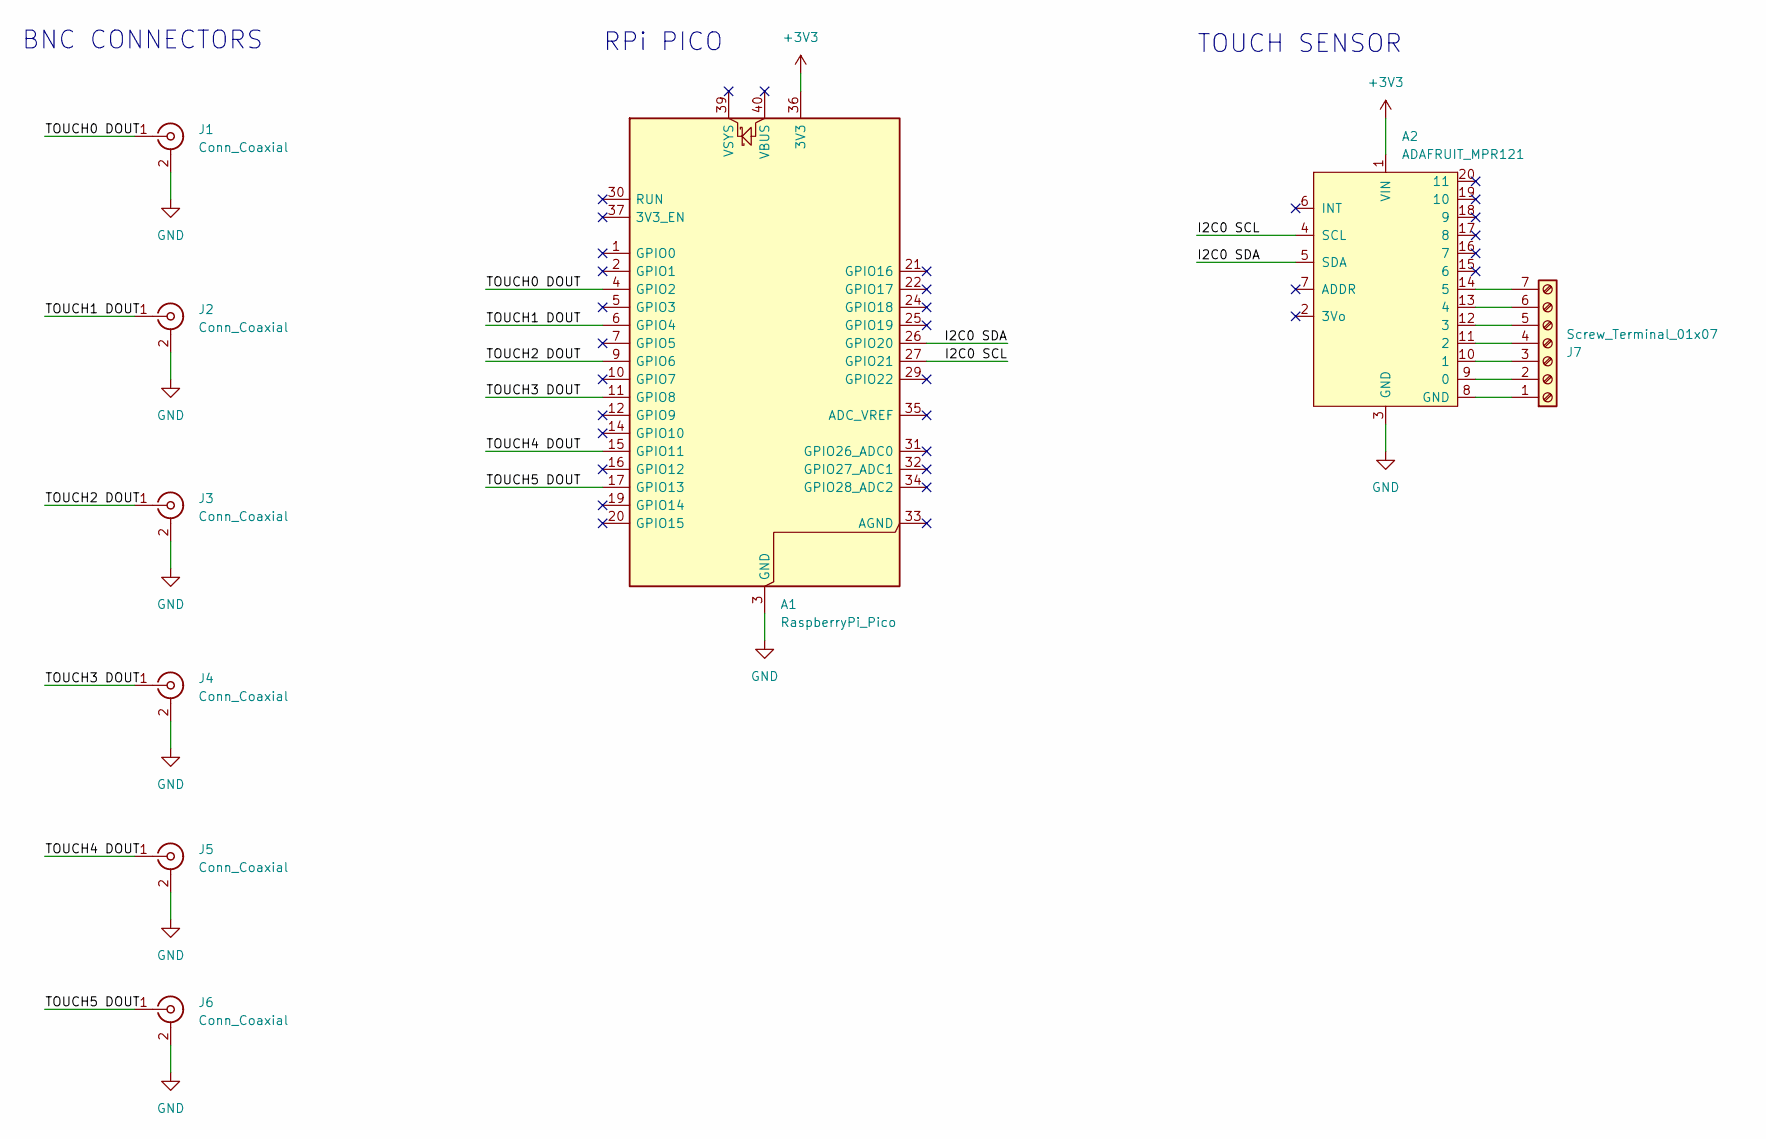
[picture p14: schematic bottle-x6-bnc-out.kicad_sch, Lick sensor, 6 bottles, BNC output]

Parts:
A1: RaspberryPi_Pico; RaspberryPi_Pico_Common_THT
A2: ADAFRUIT_MPR121
J1, J2, J3, J4, J5, J6: Conn_Coaxial; BNC_Amphenol_B6252HB-NPP3G-50_Horizontal
J7: Screw_Terminal_01x07; TerminalBlock_Phoenix_MPT-0,5-7-2.54_1x07_P2.54mm_Horizontal

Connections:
+3V3: A1.36 (3V3), A2.1 (VIN)
/I2C0 SCL: A1.27 (GPIO21), A2.4 (SCL)
/I2C0 SDA: A1.26 (GPIO20), A2.5 (SDA)
/TOUCH0 DOUT: A1.4 (GPIO2), J1.1 (In)
/TOUCH1 DOUT: A1.6 (GPIO4), J2.1 (In)
/TOUCH2 DOUT: A1.9 (GPIO6), J3.1 (In)
/TOUCH3 DOUT: A1.11 (GPIO8), J4.1 (In)
/TOUCH4 DOUT: A1.15 (GPIO11), J5.1 (In)
/TOUCH5 DOUT: A1.17 (GPIO13), J6.1 (In)
GND: A1.3 (GND), A1.8 (GND), A1.13 (GND), A1.18 (GND), A1.23 (GND), A1.28 (GND), A1.38 (GND), A2.3 (GND), J1.2 (Ext), J2.2 (Ext), J3.2 (Ext), J4.2 (Ext), J5.2 (Ext), J6.2 (Ext)
unnamed: A2.9 (0), J7.2
unnamed: A2.10 (1), J7.3
unnamed: A2.11 (2), J7.4
unnamed: A2.12 (3), J7.5
unnamed: A2.13 (4), J7.6
unnamed: A2.14 (5), J7.7
unnamed: A2.8 (GND), J7.1

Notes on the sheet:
BNC CONNECTORS
TOUCH SENSOR
RPi PICO

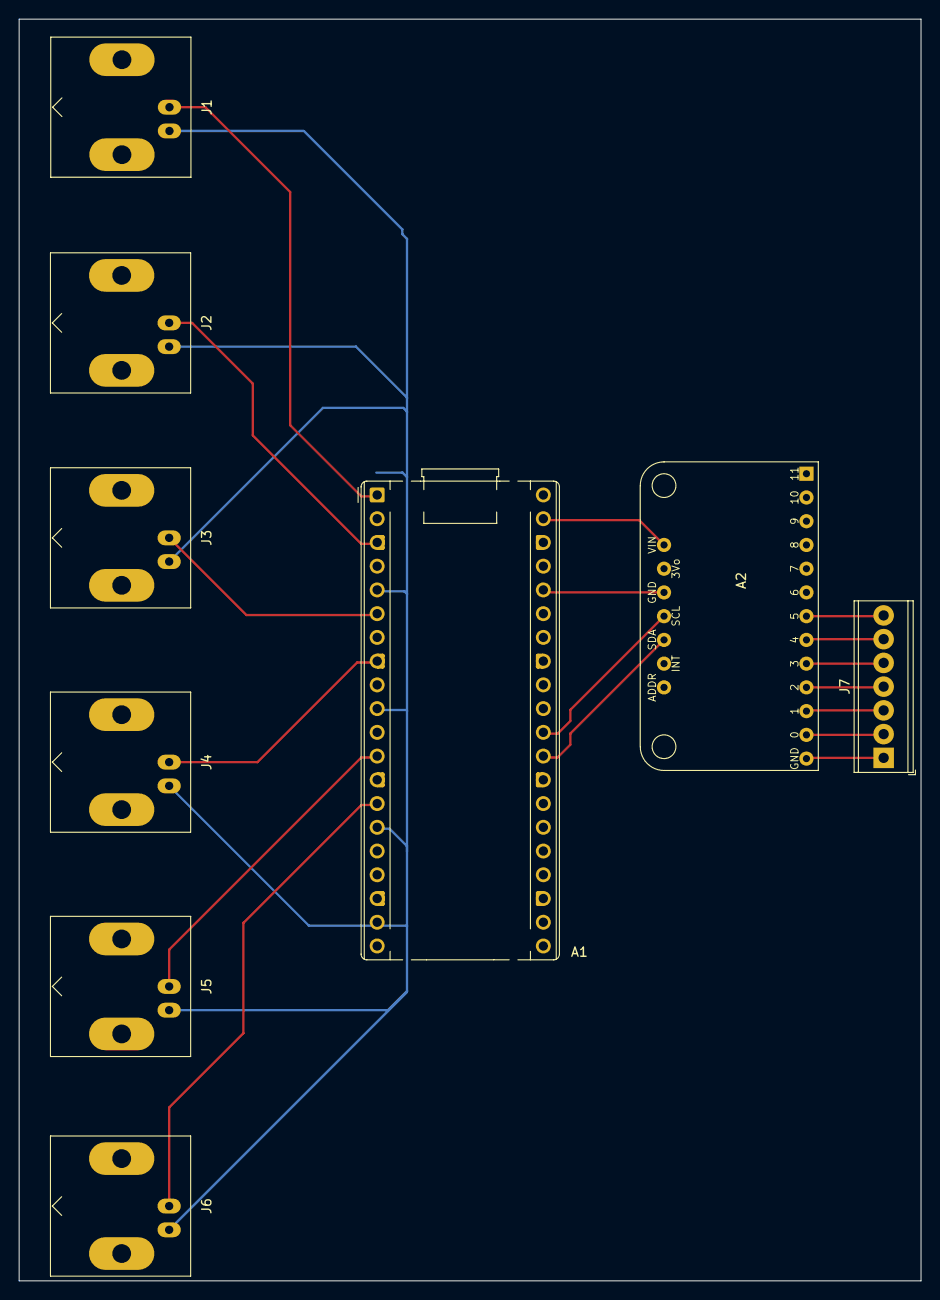
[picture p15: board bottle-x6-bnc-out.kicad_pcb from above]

Board: 2 copper layers, 96.5 x 135.0 mm, 9 parts (0 on the bottom side), 17 nets.

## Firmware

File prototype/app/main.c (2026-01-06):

#include <stdio.h>
#include "pico/stdlib.h"
#include "pico/multicore.h"
#include "pico/sync.h"
#include "hardware/i2c.h"
#include "hardware/spi.h"

#include "lcd16x2_i2c.h"
#include "mcp48x1.h"
#include "mpr121.h"

#include "settings.h"

/*
#include "pico/time.h"
absolute_time_t now;
absolute_time_t then;
int16_t tdiff;
*/

/* LCD defines */
#define LCD_I2C_PORT i2c0
#define LCD_I2C_PIN_SDA 12
#define LCD_I2C_PIN_SCL 13
#define LCD_I2C_ADDRESS 0x3E
#define LCD_I2C_FREQ 100000

/* DAC defines */
#define DAC_SPI_PORT spi0
#define DAC_SPI_BAUD 1 * 1000 * 1000 // 1 MHz
#define DAC_SPI_PIN_MOSI 3
#define DAC_SPI_PIN_CS 5
#define DAC_SPI_PIN_SCK 6

/* Touch sensor defines */
#define MPR121_I2C_PORT i2c1
#define MPR121_I2C_PIN_SDA 26
#define MPR121_I2C_PIN_SCL 27
#define MPR121_I2C_ADDRESS 0x5A
#define MPR121_I2C_FREQ 100000

/* Buttons defines */
#define BTN_UP 17
#define BTN_DOWN 18
#define BTN_LEFT 19
#define BTN_RIGHT 16

/* Digital out define */
#define TOUCH_OUT_PIN 11
const uint LED_PIN = PICO_DEFAULT_LED_PIN;

// ascii codes of useful characters
#define SPACE 32 
#define GREATER_THAN 62
#define EQUALS 61

/* LCD variables */
#define LCD_VALUE_COL 13
volatile bool needs_update = false;
uint8_t curr_setting = 0;

/* Touch sensor variables */
const uint8_t electrode = 0;
bool is_touched;
uint16_t baseline, filtered, delta_out;
int16_t delta;
// absolute_time_t now;

/* Repeating timer */
const int32_t sampling_interval_ms = 20;  // 50 Hz
bool timer_callback(repeating_timer_t *rt);

static mutex_t mtx;
struct mpr121_sensor mpr121;
struct lcd16x2 lcd;
struct mcp48x1_dac dac;

bool debounce_btn(uint8_t button){
    // From Listing 2 in www.ganssle.com/debouncing-pt2.htm
    static uint16_t state = 0;
    state = (state << 1) | !gpio_get(button) | 0xe000;
    if (state == 0xf000) return true;
    return false;
}

void lcd_put_number(uint8_t num, lcd16x2_t *lcd) {
    static uint8_t c[3];
    sprintf(c, "%3d", num);
    lcd_put_str(c, lcd);
}

void update_mpr121(struct setting *settings, uint8_t *idx,
                   lcd16x2_t *lcd, mpr121_sensor_t *mpr121) {
    switch (settings[*idx].func) {
        case FUNC_SET_TH:
            struct setting tth, rth;
            tth = get_setting(SETTING_TTH, settings);
            rth = get_setting(SETTING_RTH, settings);
            mpr121_set_thresholds(tth.value, rth.value, mpr121);
            break;
        case FUNC_SET_NHD:
            struct setting nhdr, nhdf, nhdt;
            nhdr = get_setting(SETTING_NHDR, settings);
            nhdf = get_setting(SETTING_NHDF, settings);
            nhdt = get_setting(SETTING_NHDT, settings);
            mpr121_set_noise_half_delta(nhdr.value, nhdf.value,
                                        nhdt.value, mpr121);
            break;
        case FUNC_SET_MHD:
            struct setting mhdr, mhdf;
            mhdr = get_setting(SETTING_MHDR, settings);
            mhdf = get_setting(SETTING_MHDF, settings);         
            mpr121_set_max_half_delta(mhdr.value, mhdf.value, mpr121);
            break;
    }
    // Update LCD with new value
    lcd_move_cursor(0, LCD_VALUE_COL, lcd);
    lcd_put_number(settings[*idx].value, lcd);
}

void lcd_put_setting(struct setting *settings, uint8_t *idx,
                     lcd16x2_t *lcd) {
    lcd_move_cursor(0, 0, lcd);
    lcd_put_str(settings[*idx].name, lcd);
    lcd_move_cursor(0, LCD_VALUE_COL, lcd);
    lcd_put_number(settings[*idx].value, lcd);
}

/* Core 1: Handle LCD and buttons */
void core1_entry() {
    /* Initialise buttons */
    gpio_init(BTN_UP);
    gpio_set_dir(BTN_UP, GPIO_IN);
    gpio_pull_up(BTN_UP);
    gpio_init(BTN_DOWN);
    gpio_set_dir(BTN_DOWN, GPIO_IN);
    gpio_pull_up(BTN_DOWN);
    gpio_init(BTN_LEFT);
    gpio_set_dir(BTN_LEFT, GPIO_IN);
    gpio_pull_up(BTN_LEFT);
    gpio_init(BTN_RIGHT);
    gpio_set_dir(BTN_RIGHT, GPIO_IN);
    gpio_pull_up(BTN_RIGHT);

    /* Initialise I2C for LCD */
    i2c_init(LCD_I2C_PORT, LCD_I2C_FREQ);
    gpio_set_function(LCD_I2C_PIN_SDA, GPIO_FUNC_I2C);
    gpio_set_function(LCD_I2C_PIN_SCL, GPIO_FUNC_I2C);
    gpio_pull_up(LCD_I2C_PIN_SDA);
    gpio_pull_up(LCD_I2C_PIN_SCL);
    
    /* Initialise LCD */
    lcd_init(LCD_I2C_PORT, LCD_I2C_ADDRESS, &lcd);
    lcd_put_setting(settings, &curr_setting, &lcd);
    lcd_move_cursor(0, LCD_VALUE_COL-1, &lcd);
    lcd_put_char(EQUALS, &lcd);

    /* Poll buttons */
    while (1) {
        /* Button down: next setting */
        if (debounce_btn(BTN_DOWN)) {
            curr_setting++;                
            if (curr_setting == N_SETTINGS) {
                // If already at last setting, just keep the current
                // index at that place and do nothing.
                curr_setting = (N_SETTINGS - 1);
            } else {
                lcd_put_setting(settings, &curr_setting, &lcd);
            }
        }
        /* Button up: previous setting */
        if (debounce_btn(BTN_UP)) {
            curr_setting--;
            // If curr_setting goes below 0 it will overflow back to
            // some large-ish number (because it is uint), which means
            // that we already are at the first index. If this happens
            // keep the value at 0.
            if (curr_setting > N_SETTINGS) {
                curr_setting = 0;
            } else {
                lcd_put_setting(settings, &curr_setting, &lcd);
            }            
        }
        /* Button right: increase the value of the current setting */
        if (debounce_btn(BTN_RIGHT)) {
            mutex_enter_blocking(&mtx);
            setting_increase_value(settings, &curr_setting);
            needs_update = true;
            mutex_exit(&mtx);
        }
        /* Button left: decrease the value of the current setting */
        if (debounce_btn(BTN_LEFT)) {
            mutex_enter_blocking(&mtx);
            setting_decrease_value(settings, &curr_setting);
            needs_update = true;
            mutex_exit(&mtx);
        }
        sleep_ms(20);
    }
}

int main() {
    stdio_init_all();

    /* Digital output pin */
    gpio_init(TOUCH_OUT_PIN);
    gpio_set_dir(TOUCH_OUT_PIN, GPIO_OUT);

    /* Setup the default, on-board LED */    
    gpio_init(LED_PIN);
    gpio_set_dir(LED_PIN, GPIO_OUT);

    /* Initialise I2C for touch sensor */
    i2c_init(MPR121_I2C_PORT, MPR121_I2C_FREQ);
    gpio_set_function(MPR121_I2C_PIN_SDA, GPIO_FUNC_I2C);
    gpio_set_function(MPR121_I2C_PIN_SCL, GPIO_FUNC_I2C);
    gpio_pull_up(MPR121_I2C_PIN_SDA);
    gpio_pull_up(MPR121_I2C_PIN_SCL);

    /* Initialise the touch sensor. Enable only one touch sensor
    (electrode 0) */
    mpr121_init(MPR121_I2C_PORT, MPR121_I2C_ADDRESS, &mpr121);
    mpr121_enable_electrodes(1, &mpr121);
    settings_init(settings);
    struct setting tth = get_setting(SETTING_TTH, settings);
    struct setting rth = get_setting(SETTING_RTH, settings);
    mpr121_set_thresholds(tth.value, rth.value, &mpr121);
    struct setting nhdr = get_setting(SETTING_NHDR, settings);
    struct setting nhdf = get_setting(SETTING_NHDF, settings);
    struct setting nhdt = get_setting(SETTING_NHDT, settings);
    mpr121_set_noise_half_delta(nhdr.value, nhdf.value, nhdt.value,
                                &mpr121);
    // mpr121_set_max_half_delta(mhdr, mhdf, &mpr121);
    // mpr121_set_noise_count_limit(nclr, nclf, nclt, &mpr121);

    /* Initialise SPI and DAC */
    spi_init(DAC_SPI_PORT, DAC_SPI_BAUD);
    mcp48x1_init(DAC_SPI_PORT, DAC_SPI_PIN_CS, DAC_SPI_PIN_MOSI,
                 DAC_SPI_PIN_SCK, MCP48X1_RESOLUTION_12, &dac);
    mcp48x1_set_gain(MCP48X1_GAIN_2X, &dac);

    /* Initialise mutex and start core 1 */
    mutex_init(&mtx);
    multicore_launch_core1(core1_entry);

    /* Start repeating timer */
    repeating_timer_t timer;
    add_repeating_timer_ms(-sampling_interval_ms, timer_callback, NULL,
                           &timer);

    while(1) {
        tight_loop_contents();
    }
    return 0;
}

bool timer_callback(repeating_timer_t *rt) {
    // now = get_absolute_time();
    // tdiff = to_ms_since_boot(now) - to_ms_since_boot(then);
    // then = now;

    // Check if the electrode has been touched, and read the
    // baseline and filtered data values
    mpr121_is_touched(electrode, &is_touched, &mpr121);
    mpr121_baseline_value(electrode, &baseline, &mpr121);
    mpr121_filtered_data(electrode, &filtered, &mpr121);
    delta = baseline - filtered;

    // DAC gain is set to 2x. Thus, its useful range is 0 ~ 3299 (0 ~
    // 3.3 V). Both baseline and filtered are 10-bit numbers, which
    // means that delta can be a number between -1023 and +1023.
    //
    // To output this delta value to the DAC, which is 12-bit, I add
    // 1650 to center delta at 1.65 V. This gives an output range for
    // delta of:
    //   * 1650 + 1023 = 2673 = 2.67 V
    //   * 1650 - 1023 = 627 = 0.627 V
    //
    // Multiplying delta by 1.5 extends the useful output range
    //   * 1650 + (+1023 * 1.5) = 3185 = 3.19 V
    //   * 1650 + (-1023 * 1.5) = 116 = 0.12 V
    delta_out = (uint16_t)(1650.0 + (delta * 1.5));
    
    // Output: is_touched (digital) and delta (analog) values
    gpio_put(TOUCH_OUT_PIN, is_touched);
    gpio_put(LED_PIN, is_touched);
    mcp48x1_put(delta_out, &dac);
    
    // printf("%d %d %d %d %d %d\n", baseline, filtered, delta,     
    //     settings[0].value, settings[1].value,
    //     // delta_out , mhdf,
    //     is_touched);

    // printf("%d\n", tdiff);
    
    if (needs_update && mutex_try_enter(&mtx, 0)) {
        update_mpr121(settings, &curr_setting, &lcd, &mpr121);
        needs_update = false;
        mutex_exit(&mtx);
    }
}

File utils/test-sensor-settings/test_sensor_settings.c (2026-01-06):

/*
 * Copyright (c) 2021-2025 Antonio González
 *
 * SPDX-License-Identifier: BSD-3-Clause
 */


/* MPR121 test sensor settings.

In this example only one touch sensor (electrode 0) is enabled. Then,
this electrode is polled at regular intervals and several values
reported by the sensor, notably the baseline and filtered values, are
`printf`ed to serial. These values can be read and plotted in real time
with the acompanying Python script `plotter.py`.

The various sensor settings that can be altered are exposed below. The
idea is thus to be able to play around with any of these settings and
observe how the sensor reacts differently to touch depending on these
settings.
*/

#include <stdio.h>
#include "pico/stdlib.h"
#include "hardware/i2c.h"
#include "mpr121.h"

// I2C definitions: port and pin numbers
#define I2C_PORT i2c0
#define I2C_SDA 20
#define I2C_SCL 21

// MPR121 I2C definitions: address and frequency.
#define MPR121_ADDR 0x5A
#define MPR121_I2C_FREQ 400000

int main() {
    stdio_init_all();

    // Setup the default, on-board LED.
    const uint LED_PIN = PICO_DEFAULT_LED_PIN;
    gpio_init(LED_PIN);
    gpio_set_dir(LED_PIN, GPIO_OUT);

    // Initialise I2C.
    i2c_init(I2C_PORT, MPR121_I2C_FREQ);
    gpio_set_function(I2C_SDA, GPIO_FUNC_I2C);
    gpio_set_function(I2C_SCL, GPIO_FUNC_I2C);
    gpio_pull_up(I2C_SDA);
    gpio_pull_up(I2C_SCL);

    // Initialise and autoconfigure the touch sensor.
    struct mpr121_sensor mpr121;
    mpr121_init(I2C_PORT, MPR121_ADDR, &mpr121);
    
    // Enable only one touch sensor (electrode 0).
    mpr121_enable_electrodes(1, &mpr121);

    // Initialise data variables.
    const uint8_t electrode = 0;
    bool is_touched;
    uint16_t baseline, filtered;
    int16_t delta;
    
    /* Sensor settings */

    // Thresholds (touch, release)
    // Default: 15, 10
    uint8_t tth = 15;
    uint8_t rth = 10;
    mpr121_set_thresholds(tth, rth, &mpr121);

    // Max half delta (rising, falling). Range 1~63
    // Default: 1, 1
    const uint8_t mhdr = 1;
    const uint8_t mhdf = 1;
    mpr121_set_max_half_delta(mhdr, mhdf, &mpr121);

    // Noise half delta (rising, falling, touched). Range 1~63
    // Peppe's sensor, 1, 1 ,3
    // Default: 1, 1, 1
    const uint8_t nhdr = 1;
    const uint8_t nhdf = 1;
    const uint8_t nhdt = 3;
    mpr121_set_noise_half_delta(nhdr, nhdf, nhdt, &mpr121);
    
    // Noise count limit (rising, falling, touched). Range 0~255.
    // Default: 0, 255, 0
    const uint8_t nclr = 0;
    const uint8_t nclf = 0;
    const uint8_t nclt = 0;
    mpr121_set_noise_count_limit(nclr, nclf, nclt, &mpr121);
    
    // Filter delay limit (rising, falling, touched). Range 0~255.
    // Default: 0, 2, 0
    const uint8_t fdlr = 0;
    const uint8_t fdlf = 0;
    const uint8_t fdlt = 0;
    mpr121_set_filter_delay_limit(fdlr, fdlf, fdlt, &mpr121);
    
    // Debounce (touch, release). Range 0~7.
    // Default: 0, 0
    const uint8_t tdbnc = 0;
    const uint8_t rdbnc = 0;
    mpr121_set_debounce(tdbnc, rdbnc, &mpr121);

    while(1) {
        // Check if the electrode has been touched, and read the
        // baseline and filtered data values (useful for debugging and
        // tuning the sensor).
        mpr121_baseline_value(electrode, &baseline, &mpr121);
        mpr121_filtered_data(electrode, &filtered, &mpr121);
        mpr121_is_touched(electrode, &is_touched, &mpr121);
        delta = baseline - filtered;

        // The on-board LED follows touch status.
        gpio_put(LED_PIN, is_touched);

        // Print the data.
        printf("%u %u %d %u %u %u\n", baseline, filtered, delta,
            tth, rth, is_touched * delta);

        // Pause.
        sleep_ms(50);
    }

    return 0;
}

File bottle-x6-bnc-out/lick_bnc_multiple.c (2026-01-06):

/* Copyright (c) 2024-2025 Antonio González
 * This program is free software: you can redistribute it and/or modify
 * it under the terms of the GNU General Public License as published by
 * the Free Software Foundation, either version 3 of the License, or (at
 * your option) any later version. This program is distributed in the
 * hope that it will be useful, but WITHOUT ANY WARRANTY; without even
 * the implied warranty of MERCHANTABILITY or FITNESS FOR A PARTICULAR
 * PURPOSE. See the GNU General Public License for more details. You
 * should have received a copy of the GNU General Public License along
 * with this program. If not, see <http://www.gnu.org/licenses/>.
 */

// Example of a lick sensor using 3 bottles.

#include <stdio.h>
#include "pico/stdlib.h"
#include "hardware/i2c.h"

/* Requires the pico-mpr121 libary which is available at
 * https://github.com/antgon/pico-mpr121
 */
#include "mpr121.h"

/* Touch sensor I2C definitions
 * Connect the SDA and SCL pins in the sensor to the Pico pins defined
 * here.
 */
#define MPR121_I2C_PORT i2c0
#define MPR121_I2C_PIN_SDA 20
#define MPR121_I2C_PIN_SCL 21
#define MPR121_I2C_ADDRESS 0x5A
#define MPR121_I2C_FREQ 100000

/* Define digital out pin
 * Touch (lick) data will be written to this Pico pin. Connect this pin
 * to the data acquisition system to record licking.
 */
#define OUT_PIN_0 2
#define OUT_PIN_1 4
#define OUT_PIN_2 6
#define OUT_PIN_3 8
#define OUT_PIN_4 11
#define OUT_PIN_5 13
uint32_t gpio_mask = (1 << OUT_PIN_0) | (1 << OUT_PIN_1) |
    (1 << OUT_PIN_2) | (1 << OUT_PIN_3) | (1 << OUT_PIN_4) |
    (1 << OUT_PIN_5);
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
